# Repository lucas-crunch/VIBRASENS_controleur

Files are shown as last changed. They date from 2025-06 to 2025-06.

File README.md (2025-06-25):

# 🎮 VIBRASENS_controller

**VIBRASENS_controller** est le contrôleur sans fil du système **VIBRASENS**, un dispositif de stimulation vibratoire destiné aux enfants en situation de polyhandicap.  
Ce contrôleur permet de **piloter à distance** le module vibrant via une **connexion Wi-Fi**, en ajustant précisément l'intensité, la fréquence et le canal de communication.

---

## 🧰 Composition Matérielle

### 🔩 Boîtier imprimé en 3D

- Capot (PLA)
- Base (PLA)
- Porte_composants (PLA)
- 8 vis M3 L10 tête fraisée  
  🔗 [Réf. RS Online](https://fr.rs-online.com/web/p/vis-a-metaux/9087485)

---

### ⚡ Composants électroniques

| Composant                | Référence produit | Lien |
|--------------------------|-------------------|------|
| Microcontrôleur          | M5StickC Plus 2   | [🔗 M5Stack](https://shop.m5stack.com/products/m5stickc-plus2-esp32-mini-iot-development-kit) |
| Molette haute            | M5Encoder (x1)    | [🔗 M5Stack](https://shop.m5stack.com/products/scroll-unit-with-hollow-shaft-encoder-ec10e1220501) |
| Molette basse            | M5Encoder (x1)    | [🔗 M5Stack](https://shop.m5stack.com/products/scroll-unit-with-hollow-shaft-encoder-ec10e1220501) |
| Hub I2C pour extensions  | PaHUB             | [🔗 M5Stack](https://shop.m5stack.com/products/i2c-hub-1-to-6-expansion-unit-pca9548apw) |
| Câbles de connexion      | Grove M/M (1×5 cm + 2×10 cm) | [🔗 M5Stack](https://shop.m5stack.com/products/4pin-buckled-grove-cable) |

---

## 🧾 Instructions de Montage

Les instructions de montage se trouve dans **documents_techniques** et se résume en : 
- Assemblage des composants électronique et mécanique
- Câblage des composants 

---

## 💻 Instructions de Programmation

Les instructions de programmation se trouve dans **documents_techniques** et se résume en : 
- Télécharger les différents logiciels (VSCode, Git, etc.)
- Installer les extensions (PlatformIO)
- Téléverser le code au M5StickC

---

## ⚙️ Fonctionnalités de la Télécommande

Le contrôleur permet de régler plusieurs paramètres importants du module vibrant :

### 📶 Canal Wi-Fi

- Permet la communication avec un ou plusieurs modules vibrants.
- **Obligation** : le contrôleur et le(s) module(s) doivent être configurés sur le **même canal Wi-Fi**.
- Ce réglage s’effectue via le **menu des paramètres**.

> 💡 Il est théoriquement possible de piloter plusieurs modules avec une seule télécommande, à condition qu’ils partagent le même canal.

---

### 🎚️ Intensité de vibration

- **Plage** : de **0** (aucune vibration) à **10** (intensité maximale).
- Réglage via la **molette haute** de la télécommande.

---

### 🔁 Fréquence de vibration

- **Plage** : de **0 ms** (vibration continue) à **2000 ms** (mode pulsé).
- Exemple : à 1000 ms, le module vibre pendant 1000 ms, puis s’arrête 1000 ms, etc.
- Réglage via la **molette basse** de la télécommande.



---
## 🔄 Schéma de la Machine à États



--- 

## 📂 Arborescence du dépôt

```bash
VIBRASENS_controller/
├── firmware/               # Code source Arduino/ESP-IDF
├── documents_techniques/            # Documentation technique
├── fichiers_3d/                     # Fichiers STL du boîtier
├── photos/                 # Images pour la notice de montage
└── README.md

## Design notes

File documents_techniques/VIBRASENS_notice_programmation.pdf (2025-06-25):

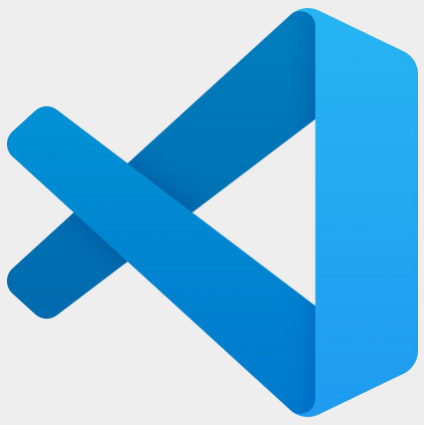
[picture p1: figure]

Pour envoyer le code à la carte M5StickC, nous avons besoin d’un environnement de développement, dans notre cas ce sera VSCODE :
https://code.visualstudio.com/download

Les codes sont stockés sur Github. Pour télécharger et utiliser le code nous auront besoin du logiciel Git : https://git-scm.com/downloads

La carte M5StickC nécessite un driver pour être programmé : https://www.silabs.com/developer-tools/usb-to-uart-bridgevcp-drivers?tab=downloads

## Installer les logiciels

Vous pouvez maintenant ouvrir VSCode, chercher “PlatformIO” dans les extensions et l’installer.

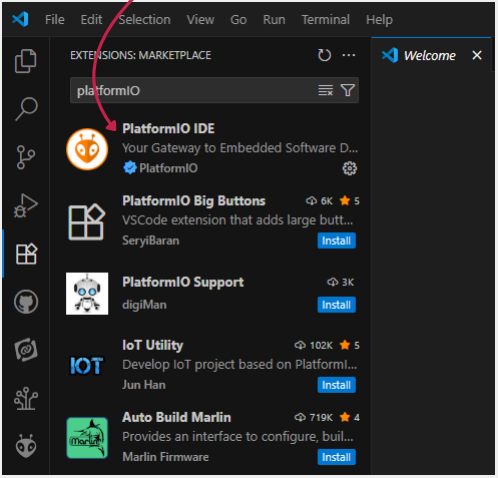
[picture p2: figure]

L’installation peut prendre 5 minutes.

## Installer les extensions

Sur le Github https://github.com/lucas-crunch/VIBRASENS_controleur, vous trouverez un bouton “Code” et vous pouvez le télécharger en cliquant sur “Download ZIP”

## Télécharger le code

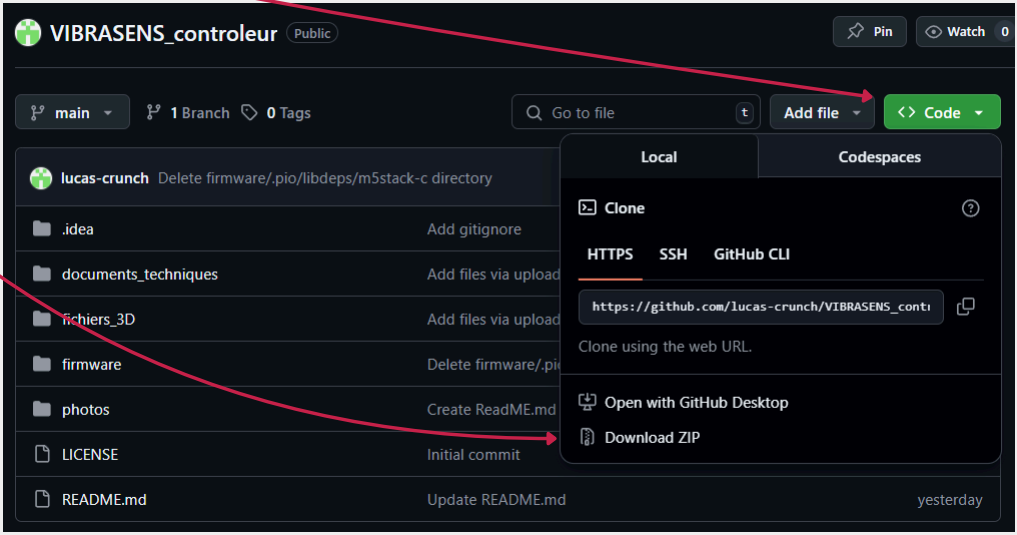
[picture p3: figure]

## Importer le code dans votre environnement de développement

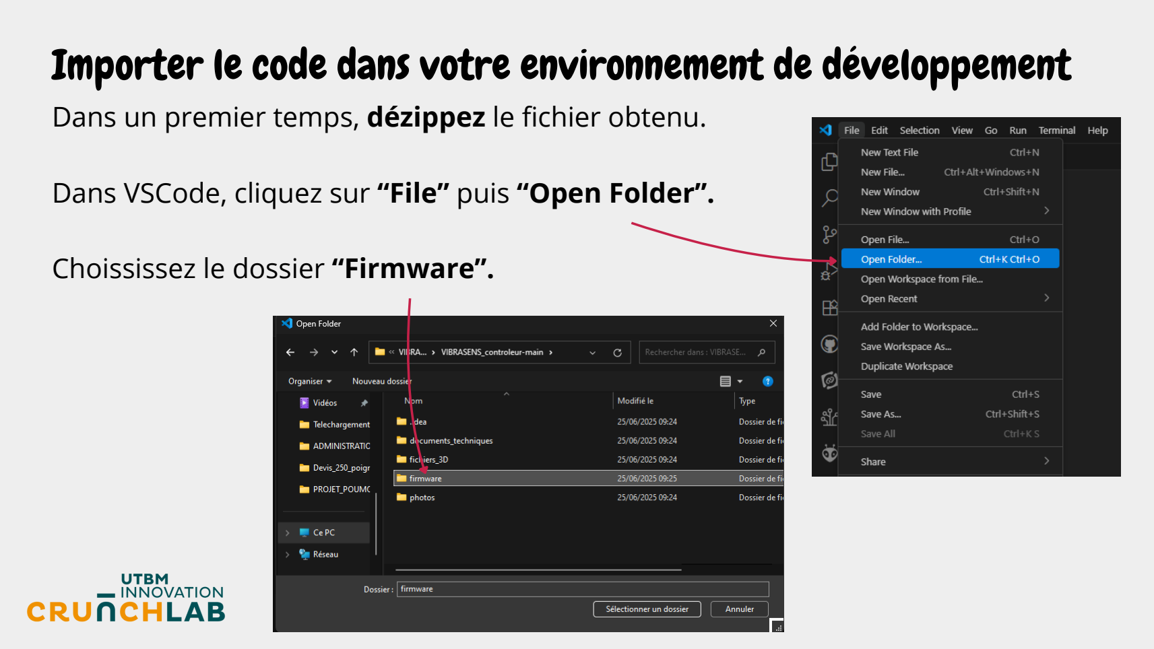
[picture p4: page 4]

Dans un premier temps, dézippez le fichier obtenu.

Dans VSCode, cliquez sur “File” puis “Open Folder”

Choississez le dossier “Firmware”

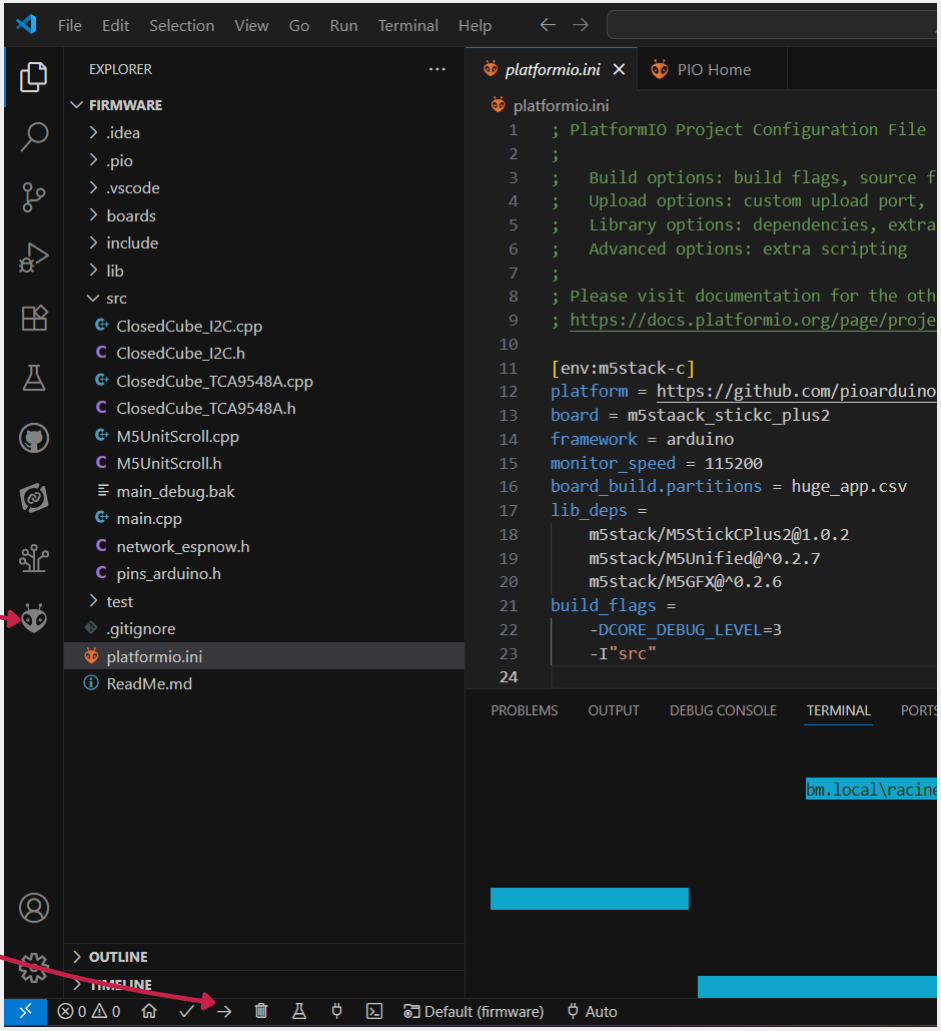
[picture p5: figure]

Cette fenêtre doit s’ouvrir.

Si le bandeau de contrôle n’est pas présent
alors cliquez sur le logo platformIO

## Importer le code dans votre environnement de développement

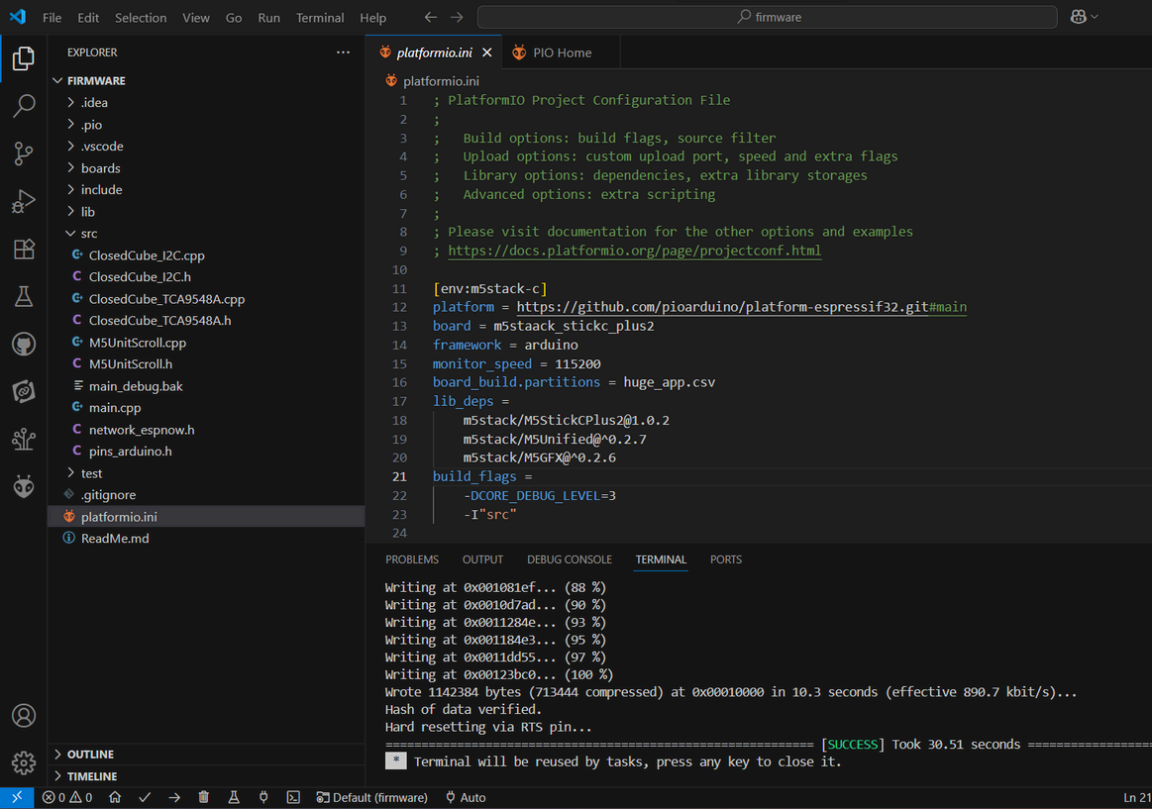
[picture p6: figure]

Reliez la carte M5StickC à l’aide d’un USB-C à l’ordinateur.

Puis cliquez sur du bandeau de commande.

Le code devrait s’envoyer à la carte et vous afficher “Success”

## Envoyer le code à la carte

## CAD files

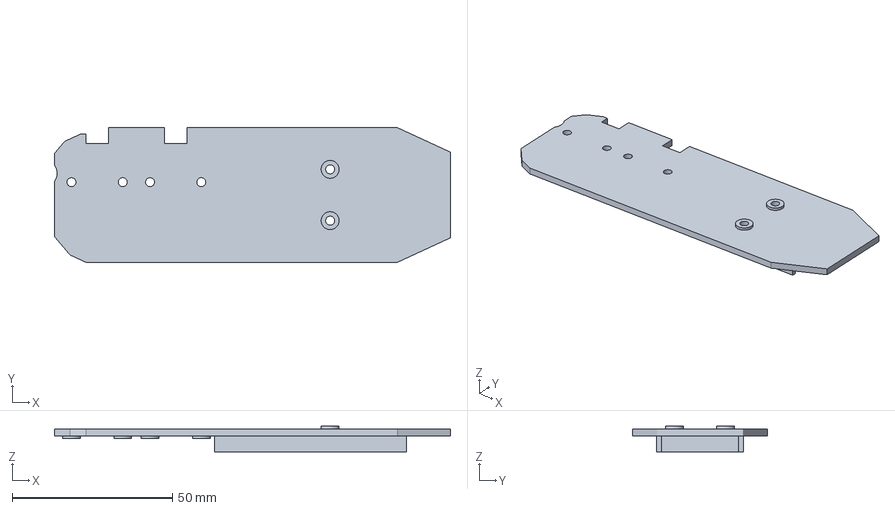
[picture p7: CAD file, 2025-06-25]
fichiers_3D/porte_composants.3mf
123.6 x 42.0 x 8.00 mm

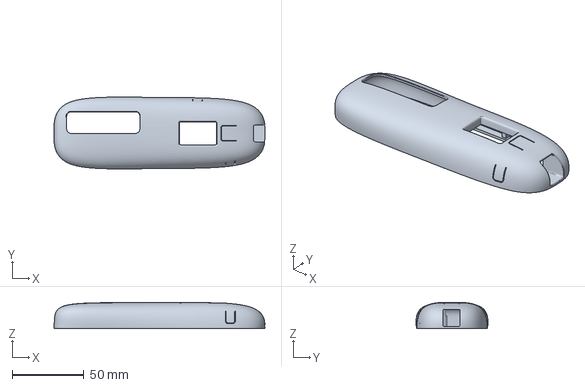
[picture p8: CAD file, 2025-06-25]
fichiers_3D/capot.3mf
147.3 x 50.1 x 18.4 mm

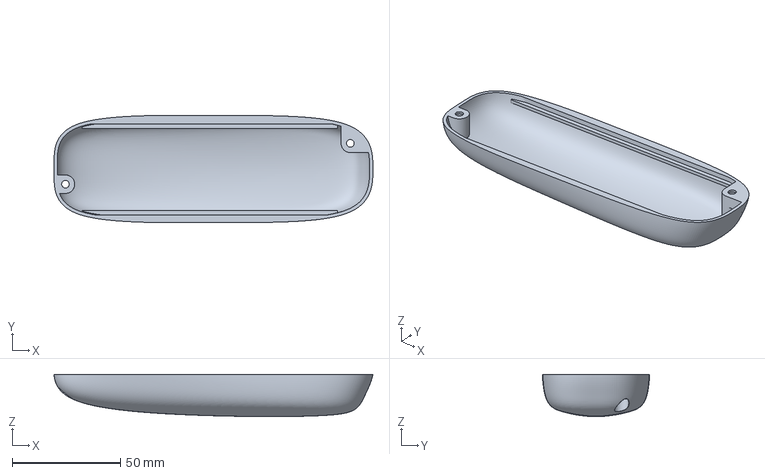
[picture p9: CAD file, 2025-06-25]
fichiers_3D/base.3mf
147.1 x 49.5 x 19.5 mm

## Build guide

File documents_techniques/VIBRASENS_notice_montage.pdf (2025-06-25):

## Matériel

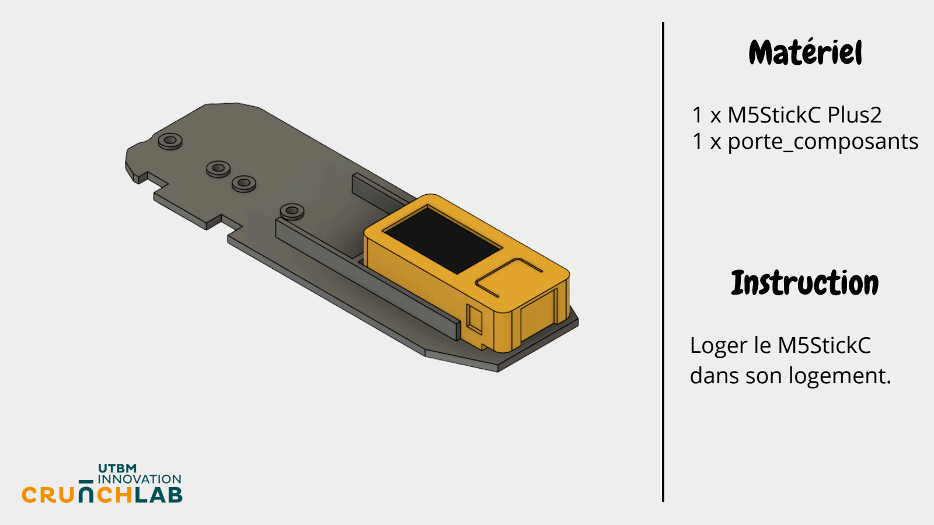
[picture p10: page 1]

1 x M5StickC Plus2
1 x porte_composants

## Instruction

Loger le M5StickC
dans son logement.

## Matériel

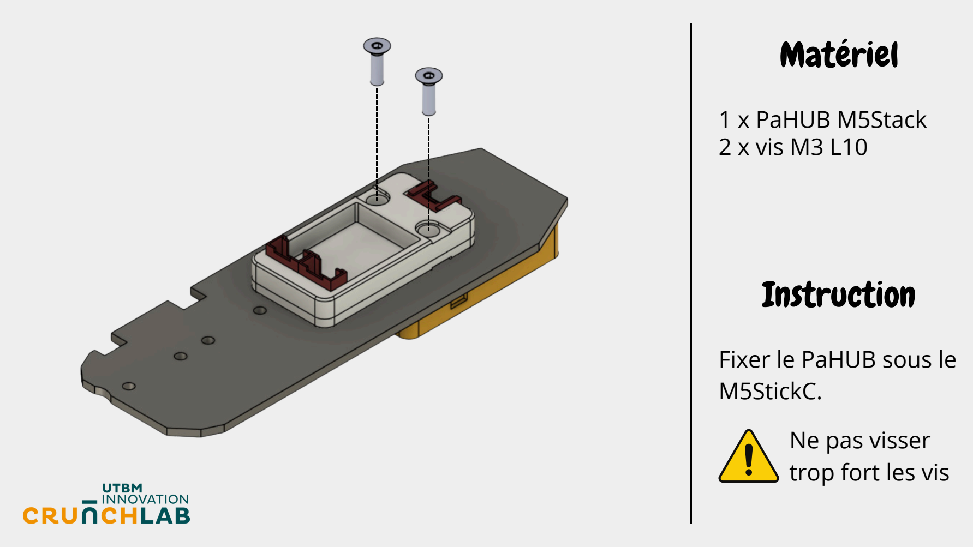
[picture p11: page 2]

1 x PaHUB M5Stack
2 x vis M3 L10

## Instruction

Fixer le PaHUB sous le
M5StickC.
Ne pas visser
trop fort les vis

## Matériel

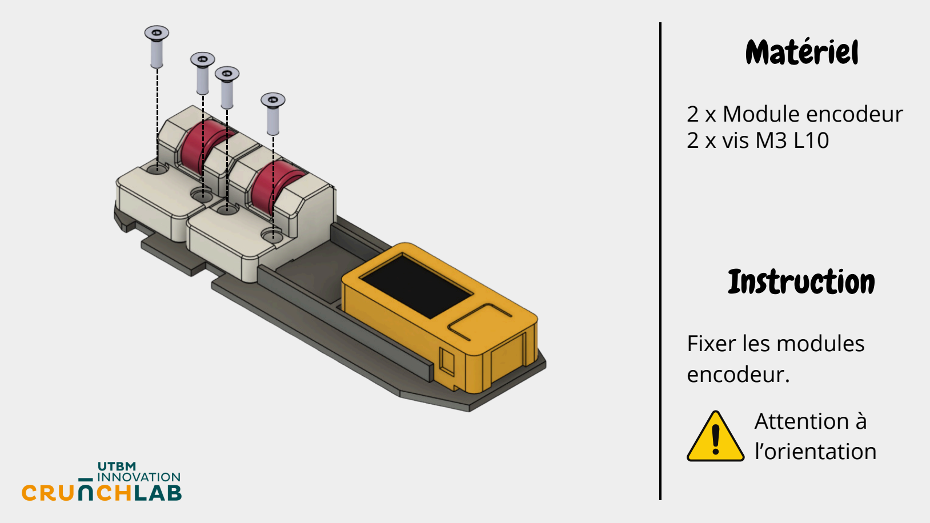
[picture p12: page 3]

2 x Module encodeur
2 x vis M3 L10

## Instruction

Fixer les modules
encodeur.
Attention à
l’orientation

## Matériel

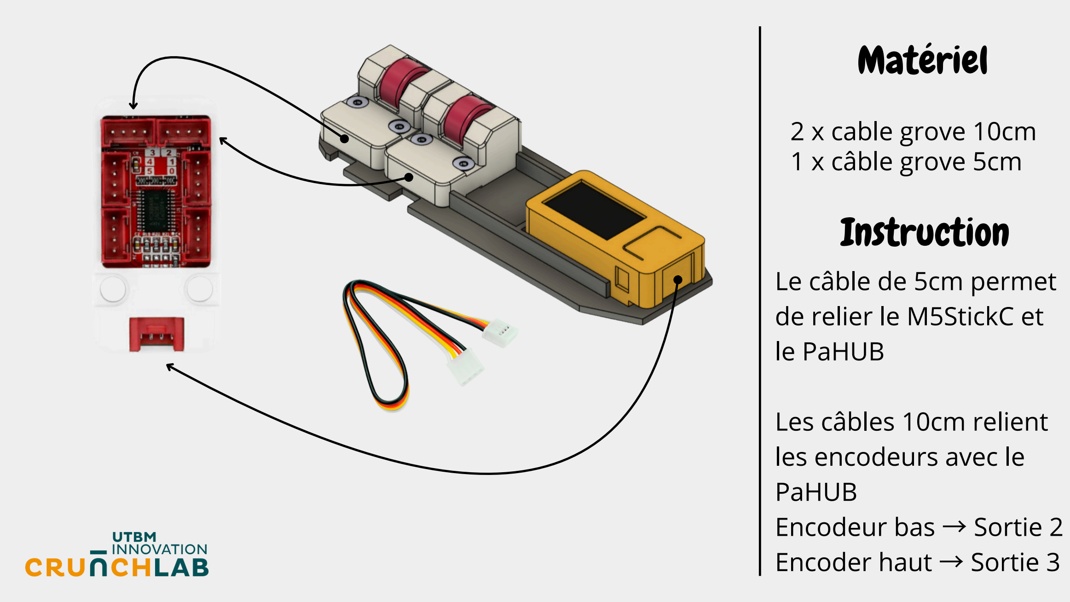
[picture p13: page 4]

2 x cable grove 10cm
1 x câble grove 5cm

## Instruction

Le câble de 5cm permet
de relier le M5StickC et
le PaHUB

Les câbles 10cm relient
les encodeurs avec le
PaHUB
Encodeur bas → Sortie 2
Encoder haut → Sortie 3

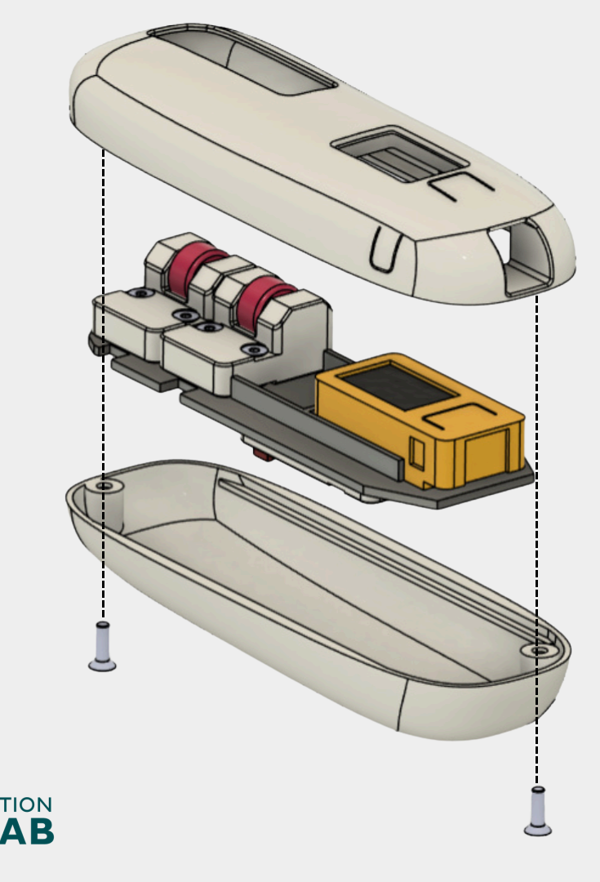
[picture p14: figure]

## Matériel

1 x capot
1 x base

## Instruction

Fixer la base avec le
capot.

2 x vis M3 L10

Attention à
l’ajustement
